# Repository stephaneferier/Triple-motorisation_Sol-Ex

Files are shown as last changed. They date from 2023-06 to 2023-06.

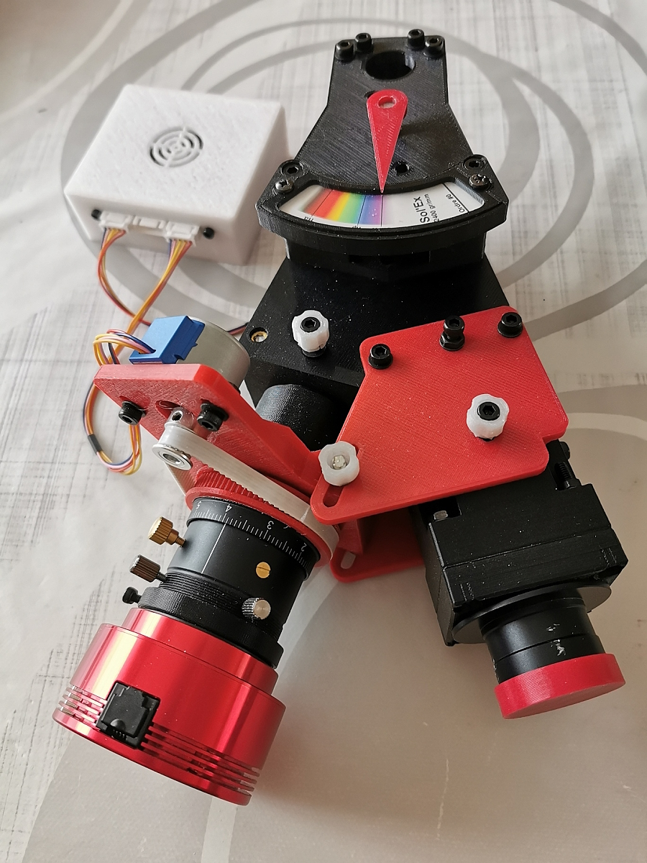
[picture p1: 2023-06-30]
focuser caméra.jpg

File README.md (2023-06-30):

# SolEx Motorisation (English version below)

Le Sol'Ex de Christian Buil est un "Explorateur solaire" qui permet d'imager le soleil dans une longueur d'onde souhaitée, allant du proche UV au proche IR.
La construction de ce spectroscope est détaillée sur son site internet: http://www.astrosurf.com/solex/sol-ex-objet.html
La partie traitement informatique du signal enregistré est confiée soit à i-Spec (programme écrit par Christian Buil), soit par Inti, programme développé par Valérie Desnoux. Ces deux programmes sont référencés sur le site Sol'Ex, et des mises à jour régulières sont publiées.
Un forum d'échange est aussi disponible à l'adresse : https://groups.io/g/Solex-project La communauté y est très active.

Nous vous présentons ici un appendice développé conjointement par Jean Brunet, Pascal Berteau et Stéphane Ferier, qui permet de motoriser le Sol'Ex initial, ainsi que la prise en charge de la mise au point de la lunette astro et du focuseur hélicoïdal de la caméra d'acquisition!
Le but ici est d'apporter une facilité à voyager parmi les raies spectrales qui composent le spectre solaire, au moyen d'un software développé pour Android/IOS, basé sur une page web gérée par le software. Des raies spectrales d'intérêt majeur y sont définies, et accessibles d'un simple clic.

Le programme ainsi que les fichiers .stl de construction du support de motorisation sont "open-source", et toute amélioration est la bienvenue.
Pour un complément d'informations sur la manière d'uploader les fichiers .ino dans l'ESP, veuillez trouver les informations utiles sur le projet initial "Motorisation du Sol'Ex" disponible ici: https://github.com/stephaneferier/SolEx-Motorisation
Vous y trouverez un fichier .pdf qui décrit en détails comment réaliser cette motorisation, comment monter le système sur le Sol'Ex, comment réaliser le montage électronique de pilotage, comment uploader le software dans l'ESP32 utilisé, ainsi que coment utiliser le software. Ce fichier .pdf est disponible en Français, et en Anglais.

# SolEx Motorization (English Version)

Christian Buil's Sol'Ex is a "solar explorer" which allows the sun to be imaged in a desired wavelength, ranging from near UV to near IR.
The construction of this spectroscope is detailed on its website: http://www.astrosurf.com/solex/sol-ex-objet.html
The computer processing part of the recorded signal is entrusted either to i-Spec (program written by Christian Buil), or by Inti, program developed by Valérie Desnoux. These two programs are referenced on the Sol'Ex site, and regular updates are published.
An exchange forum is also available at: https://groups.io/g/Solex-project The community is very active there.

We present here an appendix developed jointly by Jean Brunet, Pascal Berteau and Stéphane Ferier, which makes it possible to motorize the initial Sol'Ex, as well as the management of the focusing of the astro telescope and the helical focuser of the camera. acquisition!
The goal here is to facilitate travel among the spectral lines that make up the solar spectrum, using software developed for Android/IOS, based on a web page managed by the software. Spectral lines of major interest are defined there, and accessible with a simple click.

The program as well as the motorization support construction .stl files are "open-source", and any improvement is welcome.
For more information on how to upload .ino files in the ESP, please find the useful information on the initial project "Motorization of the Sol'Ex" available here: https://github.com/stephaneferier/ SolEx-Motorization
You will find a .pdf file that describes in detail how to make this motorization, how to mount the system on the Sol'Ex, how to make the electronic pilot assembly, how to upload the software in the ESP32 used, as well as how to use the software. . This .pdf file is available in French and English.

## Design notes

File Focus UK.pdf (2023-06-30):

## Sol'Ex, camera focus with stiffeners

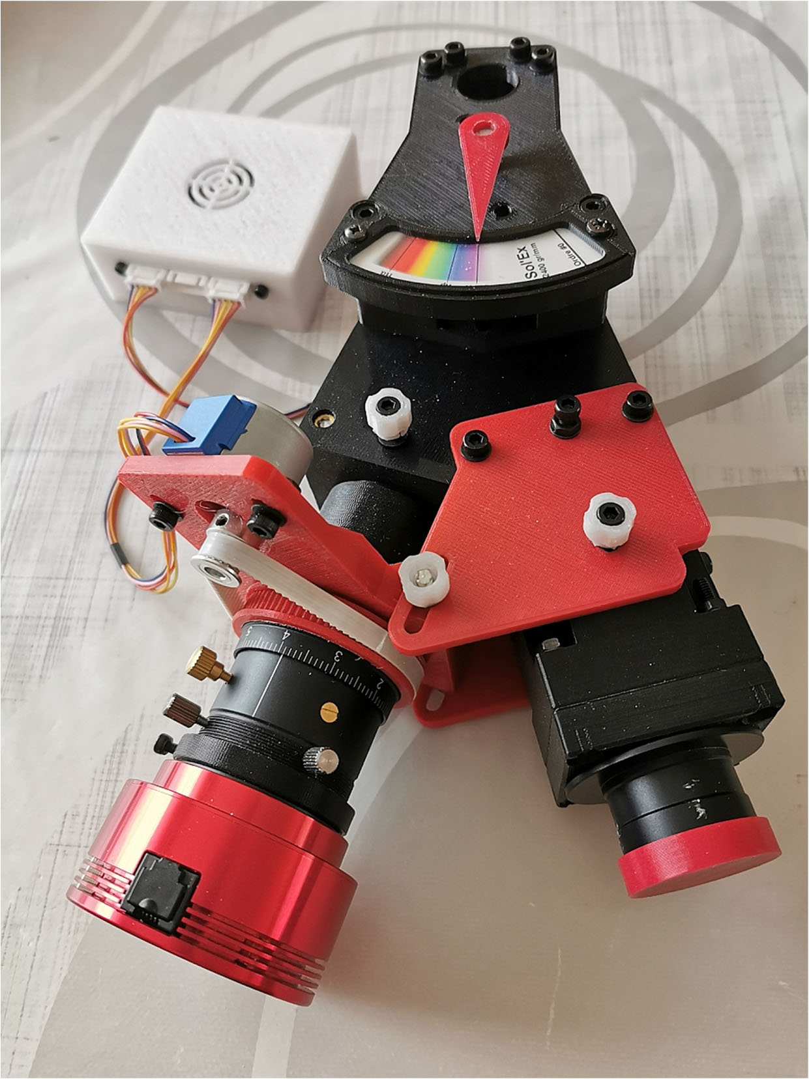
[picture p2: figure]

On the left the motor control box
The focuser has two functions, stiffening Sol'Ex and supporting the engine.

The fixation including the two symmetrical plates and the ring on the ZWO helical eyepiece holder was proposed on the Sol'Ex list by Gilles Leroy.
https://drive.google.com/drive/folders/1wKxa_FFrP0awlb0r-Le1xkUWJgxMOKyo

The GT2 belt wheel comes from Julien Lecomte's focuser also seen on the list. GitHub - jlecomte/ascom-oag-focuser: Open Source ASCOM-Compatible OAG Focuser For Astrophotography

I chose the belt drive for more precision.

I took the ring from the ZWO and added the motor mount. There is a 4mm ruthex on the side to secure the motor ring. A threaded rod encloses the two symmetrical stiffeners with the motor support ring. It will probably be necessary to play a little with sandpaper to adjust the two rings as not to have movement.

The turntable supports the 28BYJ-48 engine on which a small GT 2 sprocket is added. A GT2 belt 6 mm wide and 200 mm long connects the gear wheel to the engine.
The motor is fixed with two screws and two washers. The nuts are on the engine side that blocks them. Tighten the belt moderately when mounting so as not to weaken the small engine.

Good achievement to all,
Jean Brunet, Pascal Berteau, Stéphane Ferier.

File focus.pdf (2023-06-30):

## Sol'Ex, focuser caméra avec raidisseurs


A gauche le boîtier de commande des moteurs
Le focuser a deux fonctions, rigidifier Sol'Ex et supporter le moteur.

La fixation incluant les deux platines symétriques et la bague sur le porte oculaire hélicoïdal ZWO a été proposée sur la liste Sol'Ex par Gilles Leroy.
https://drive.google.com/drive/folders/1wKxa_FFrP0awlb0r-Le1xkUWJgxMOKyo

La roue pour courroie GT2 vient du focuser de Julien Lecomte vu aussi sur la liste.
GitHub - jlecomte/ascom-oag-focuser: Open Source ASCOM-Compatible OAG Focuser For Astrophotography
J'ai choisi la transmission par courroie pour plus de précision.

J'ai repris la bague du ZWO et j'ai ajouté le support du moteur. Il y a un ruthex de 4 mm sur le côté pour fixer la bague du moteur. Une tige filetée enserre les deux raidisseurs symétriques avec la bague support moteur. Il faudra sans doute un peu jouer du papier de verre pour ajuster les deux bagues qui ne doivent pas avoir de jeu.

La platine supporte le moteur 28BYJ-48 sur lequel on ajoute un petit pignon GT2. Une courroie GT2 de 6 mm de large et de 200 mm de long relie la roue dentée au moteur.
La fixation du moteur se fait avec deux vis et deux rondelles. Les écrous sont du côté du moteur qui les bloque. Tendre modérément la courroie au montage pour ne pas fragiliser le petit moteur.

Bonne réalisation à tous,
Jean Brunet, Pascal Berteau, Stéphane Ferier.

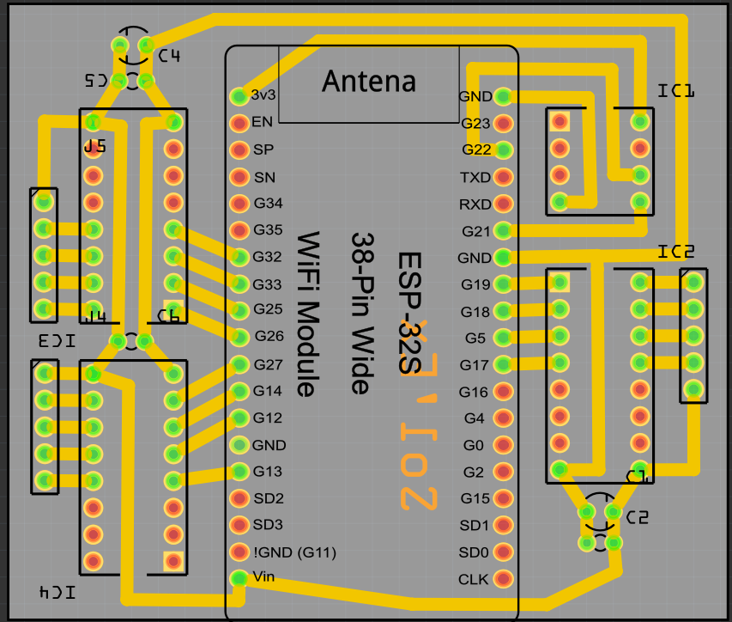
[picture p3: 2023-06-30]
Typon.png

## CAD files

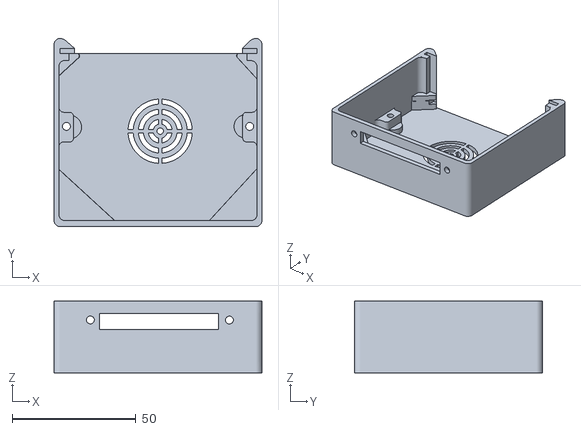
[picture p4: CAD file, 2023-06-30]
boitier3m.stl
84.1 x 76.1 x 29.1

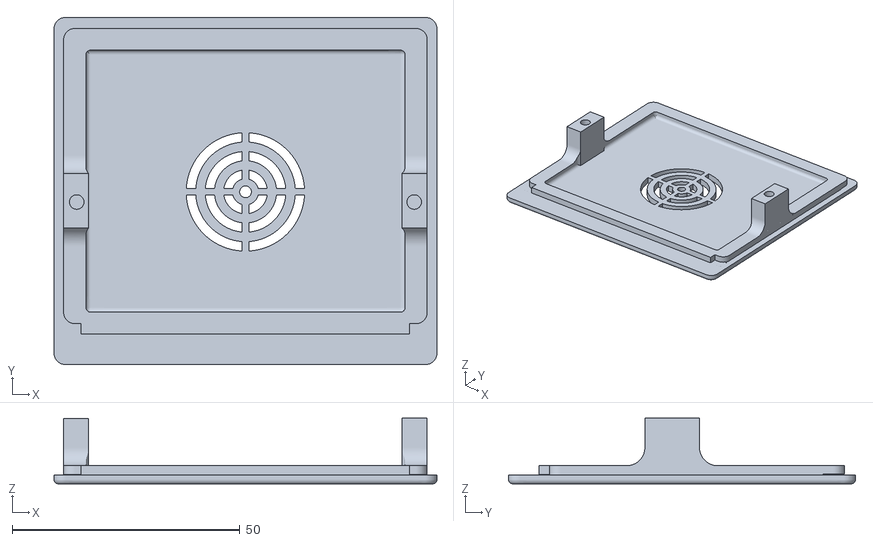
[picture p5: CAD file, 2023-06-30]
couvercle3m.stl
84.1 x 76.2 x 14.5

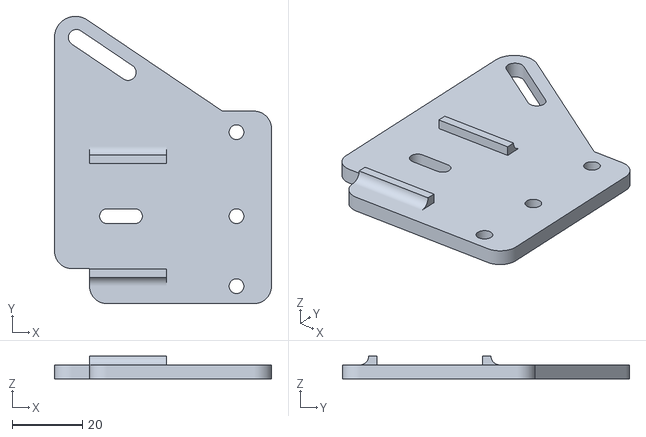
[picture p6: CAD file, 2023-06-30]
Renfort__Side_B_ZWO.stl
62.0 x 82.1 x 6.50

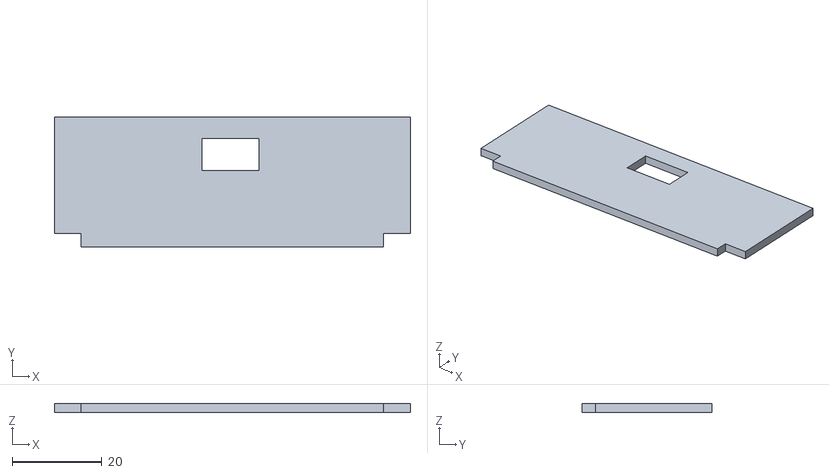
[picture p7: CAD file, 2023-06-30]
face3m.stl
79.4 x 29.0 x 2.00

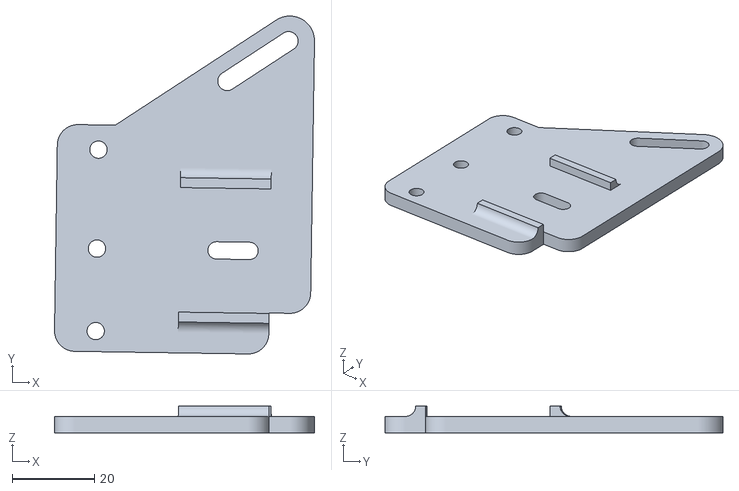
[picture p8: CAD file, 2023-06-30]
Renfort__Side_A_ZWO.stl
63.1 x 81.9 x 6.50

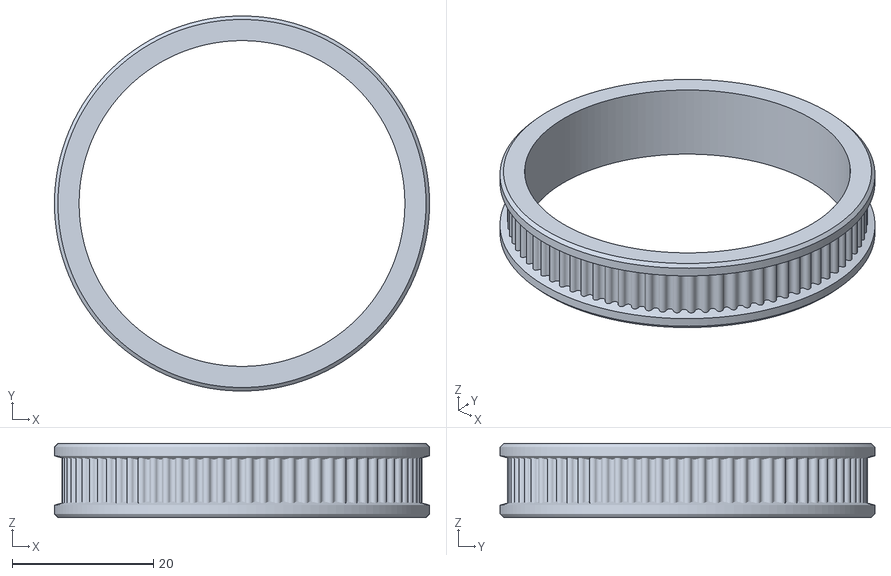
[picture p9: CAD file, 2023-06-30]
Focuser_Pulley.stl
53.2 x 53.2 x 10.5

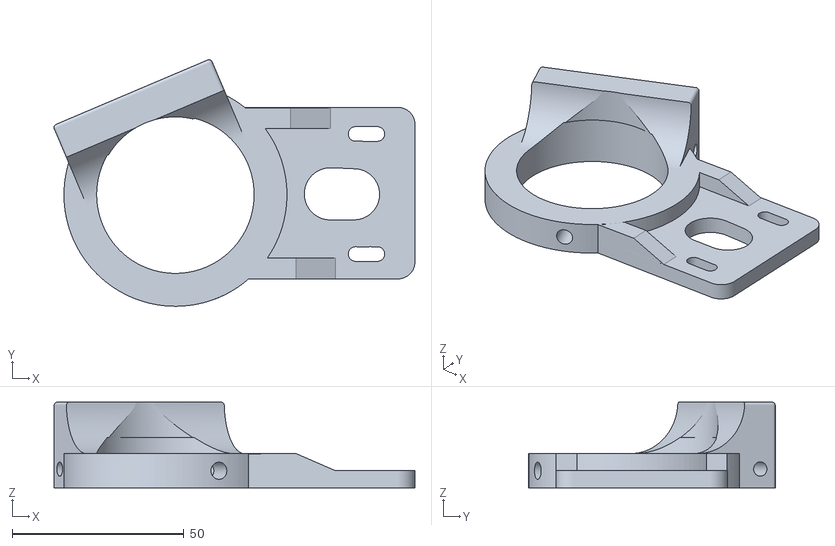
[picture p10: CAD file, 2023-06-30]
platine moteur.stl
105.2 x 71.9 x 25.0

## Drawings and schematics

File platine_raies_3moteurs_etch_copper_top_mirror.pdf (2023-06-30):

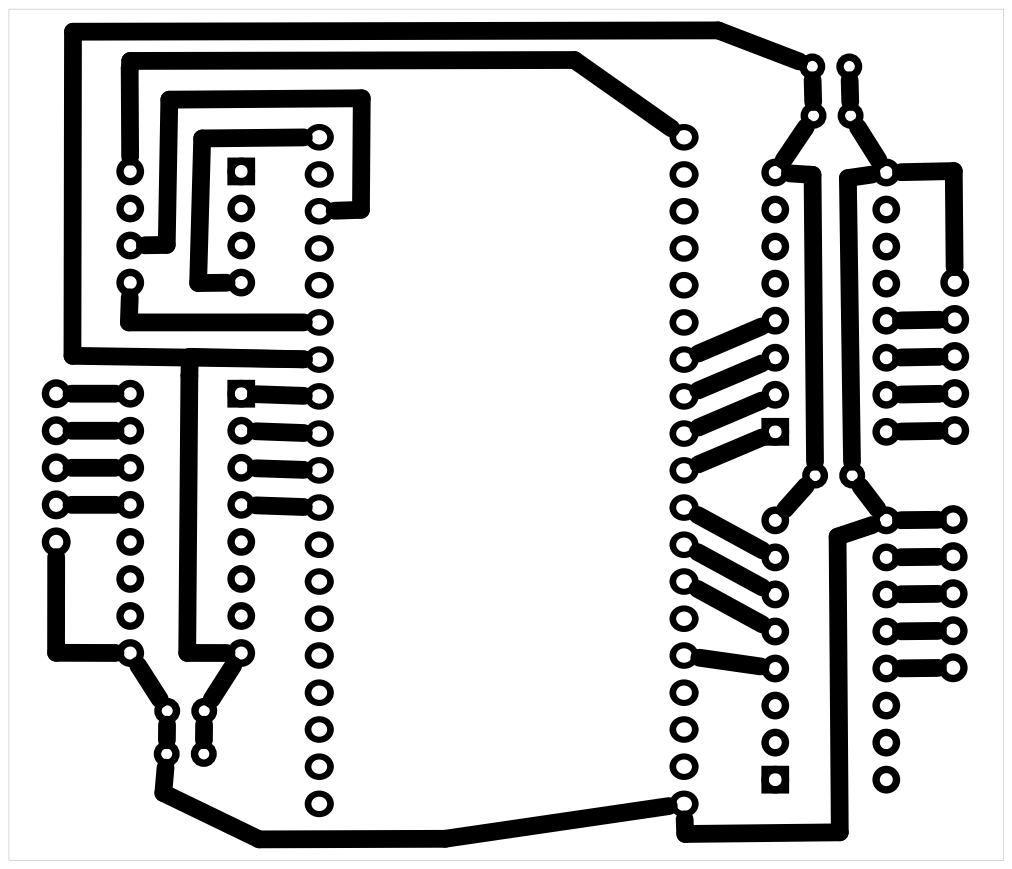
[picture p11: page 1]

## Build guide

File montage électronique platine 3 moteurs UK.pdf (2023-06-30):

Electronic stage with 3 motors

PCB assembly

You will find in the sharing the typons of the printed circuit boards in pdf format for those who wish to order the circuits (see the possible resellers on the internet) or engrave them themselves by sunstroke. For those who have a PCB burner, these files are also provided in Gerber format.

Once in possession of the printed circuit boards, assembly can begin.

Take the plates supplied with the motors and remove the ULN2003 ICs, desolder the IC bracket and the white connector. However, I give a list of all the components to buy from Conrad. The ESP32 DEV Kit is available on Amazon.

Start by soldering the 8-pin and 16-pin IC brackets, then solder the ESP32's two support strips. Finish with the capacitors, pay attention to the direction of chemical capacities, on the photo the positive (+) is indicated. Weld the 3 clusters of 5 wires at the output of the ULN 2003.

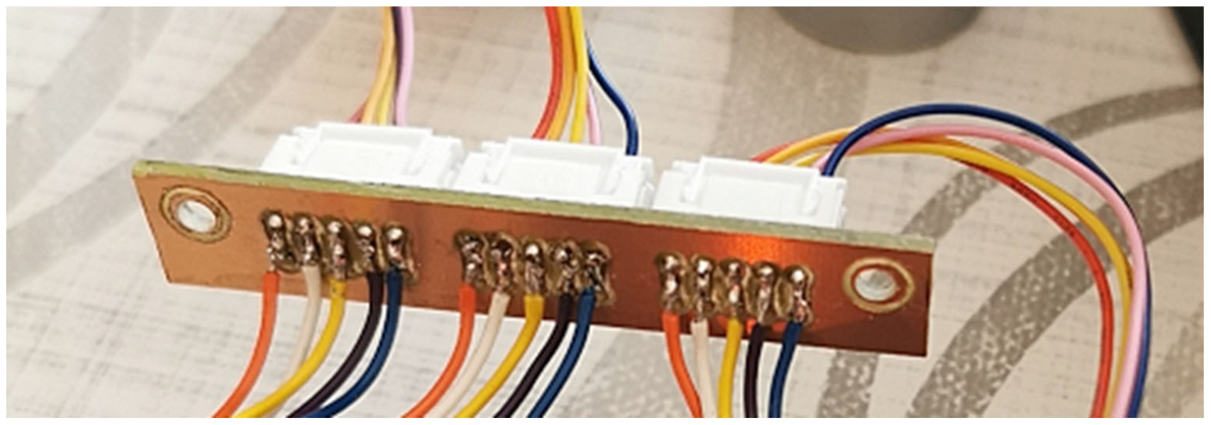
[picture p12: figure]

The connectors are to be welded in the alignment of the two screw holes, keying upwards. The wires are soldered directly onto the tracks of the mini circuit board.

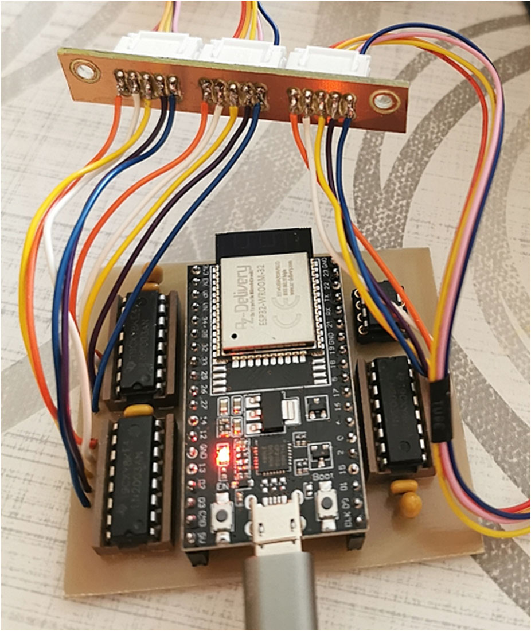
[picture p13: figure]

Take care to respect the order of the threads
according to their color. Orange is the +
noted on the typon.

Place ULN 2003 and 24LC01 on
their supports, pin 1 is
identified on the typon (see below). the

ESP32 is to place the USB connector directed outside of the printed circuit board.

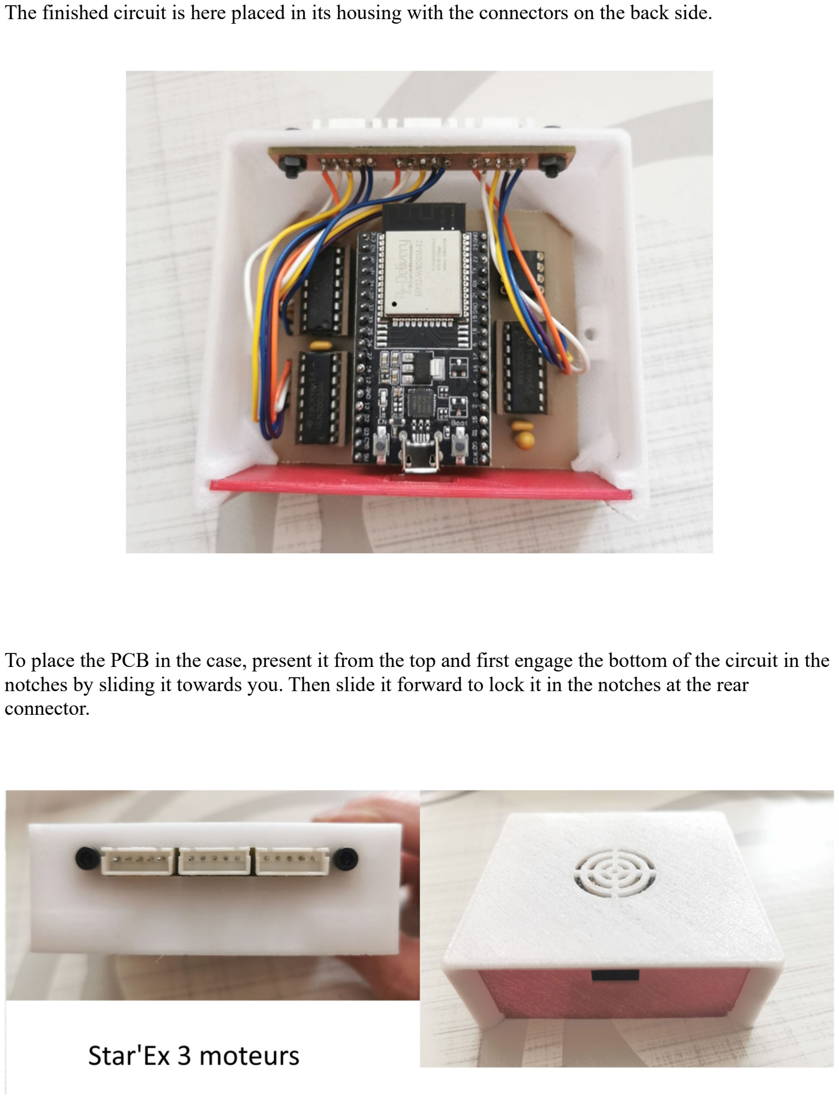
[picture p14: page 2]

The finished circuit is here placed in its housing with the connectors on the back side.

To place the PCB in the case, present it from the top and first engage the bottom of the circuit in the notches by sliding it towards you. Then slide it forward to lock it in the notches at the rear connector.

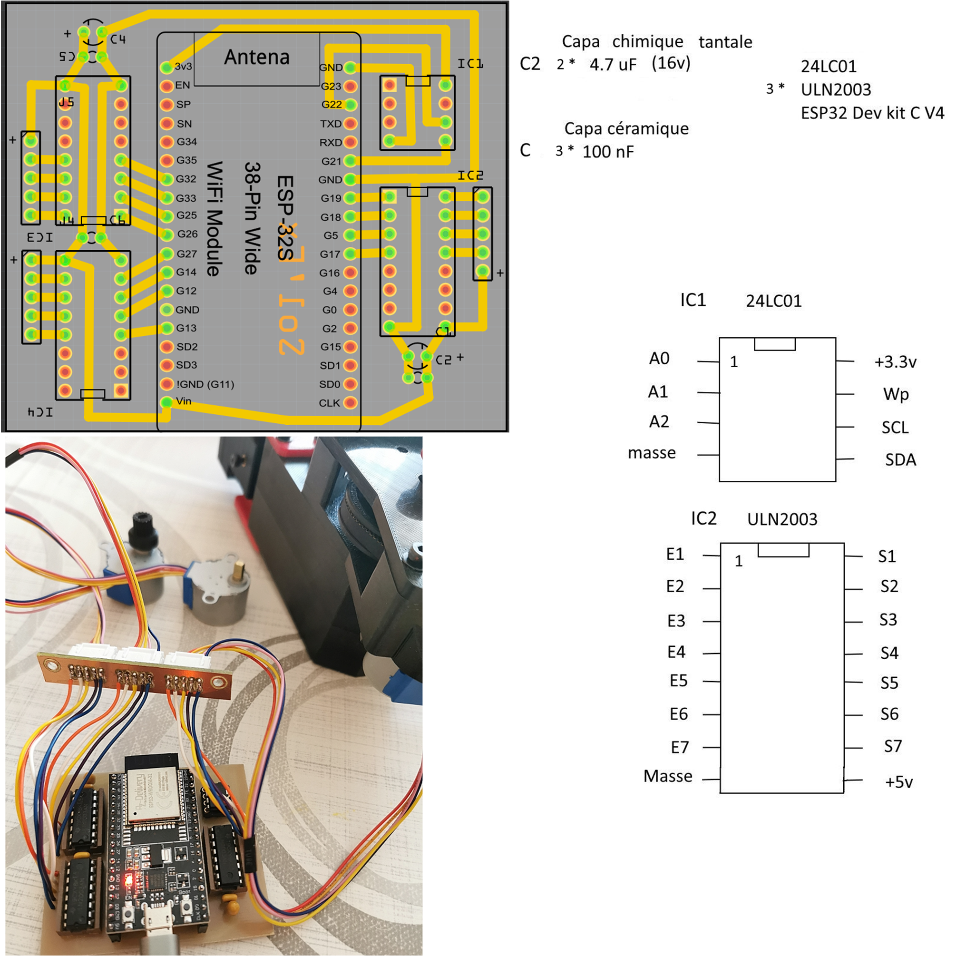
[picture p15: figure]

List of components to buy from Conrad (or other dealers of your choice).

3 * 100 nF Kemet C320C104M5U5TA+ 100 nF 50 V 20 % Z5U 1 pc(s) - Conrad Electronic France

2 * 4.7 uF TANCAP CA42-475M035AB Tantalum Capacitor THT 2.5 mm 4.7 μF 35 V 20% (W x
H) 5.5 mm x 14 mm 1 pc(s) - Conrad Electronic France

8-pin bracket Integrated circuit holder 7.62 mm, 2.54 mm Number of poles (num): 8 precision contacts 1 pc(s) - Conrad Electronic France

3 * 16-pin Support econ connect Integrated Circuit Support Number of poles (num): 16 precision contacts 1 pc(s) Tube - Conrad Electronic France

Strips for ESP32 (provide two) Connfly Female bar (standard) Number of rows: 1 Number of poles per row: 20 DS1023-1*20S21 1 pc(s) - Conrad Electronic France

24LC01 Microchip Technology 24LC01B/P CI Memory DIP-8 EEPROM 1 ko 128 x 8 - Conrad Electronic France

3 * ULN2003 STMicroelectronics Transistor dipolar (BJT) - Matrix ULN2003A DIP-16 7 NPN -Darlington - Conrad Electronic France

3 * 5-pin Connector Male Case (Turntable) econ connect W33S5 Total Bbr Poles 5 Steps: 2.5 mm 1 pc(s) - Conrad Electronic France

ESP32-WROOM-32 Dev kit C4: https://www.amazon.fr/dp/B08BTS62L7

Good achievement to all,
Jean Brunet
Pascal Berteau
Stéphane Ferier

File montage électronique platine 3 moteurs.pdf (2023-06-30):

Platine électronique avec 3 moteurs

Montage du circuit imprimé

Vous trouverez dans le partage les typons des circuits imprimés au format pdf pour ceux qui souhaitent commander les circuits (voir les éventuels revendeurs sur internet) ou les graver euxmêmes par insolation. Pour ceux qui ont une graveuse de circuit imprimé, ces fichiers sont aussi fournis au format Gerber.

Une fois en possession des circuits imprimés, on peut entamer le montage.

Prendre les platines fournies avec les moteurs et retirez les circuits intégrés ULN2003, dessoudez le support du circuit intégré et le connecteur blanc. Toutefois, je donne une liste de tous les composants à acheter chez Conrad. L'ESP32 DEV Kit est disponible sur Amazon.

Commencez par souder les supports des circuits intégrés 8 broches et 16 broches, puis soudez les deux barrettes support de l'ESP32. Terminez par les condensateurs, attention au sens des capacités chimiques, sur la photo le positif (+) est indiqué. Soudez les 3 grappes de 5 fils en sortie des ULN 2003.

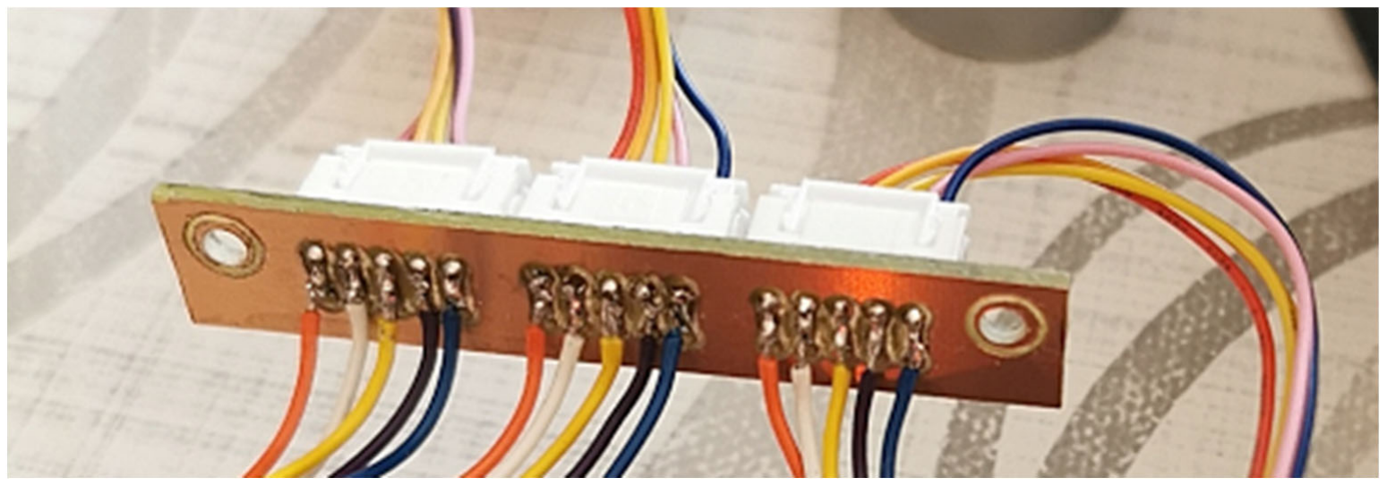
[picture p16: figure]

Les connecteurs sont à souder dans l'alignement des deux trous de vis, détrompeurs vers le haut. Les fils sont soudés directement sur les pistes
du mini circuit imprimé.

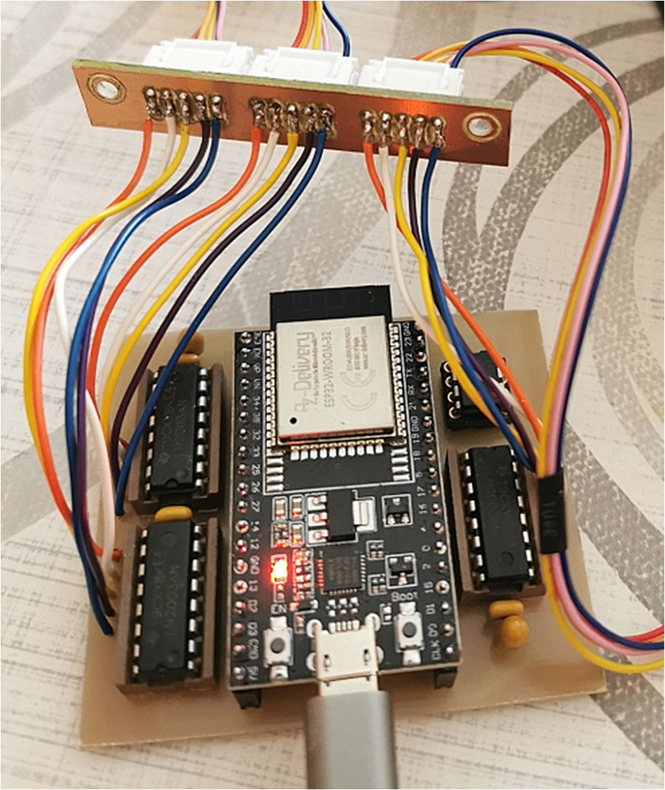
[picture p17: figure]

Bien respecter l'ordre des fils
selon leur couleur. Le orange est le +
noté sur le typon.

Placez les ULN 2003 et le 24LC01 sur leurs supports, la broche 1 est identifiée sur le typon (voir ci-dessous).

l'ESP32 est à placer le connecteur USB vers le bas du circuit imprimé.

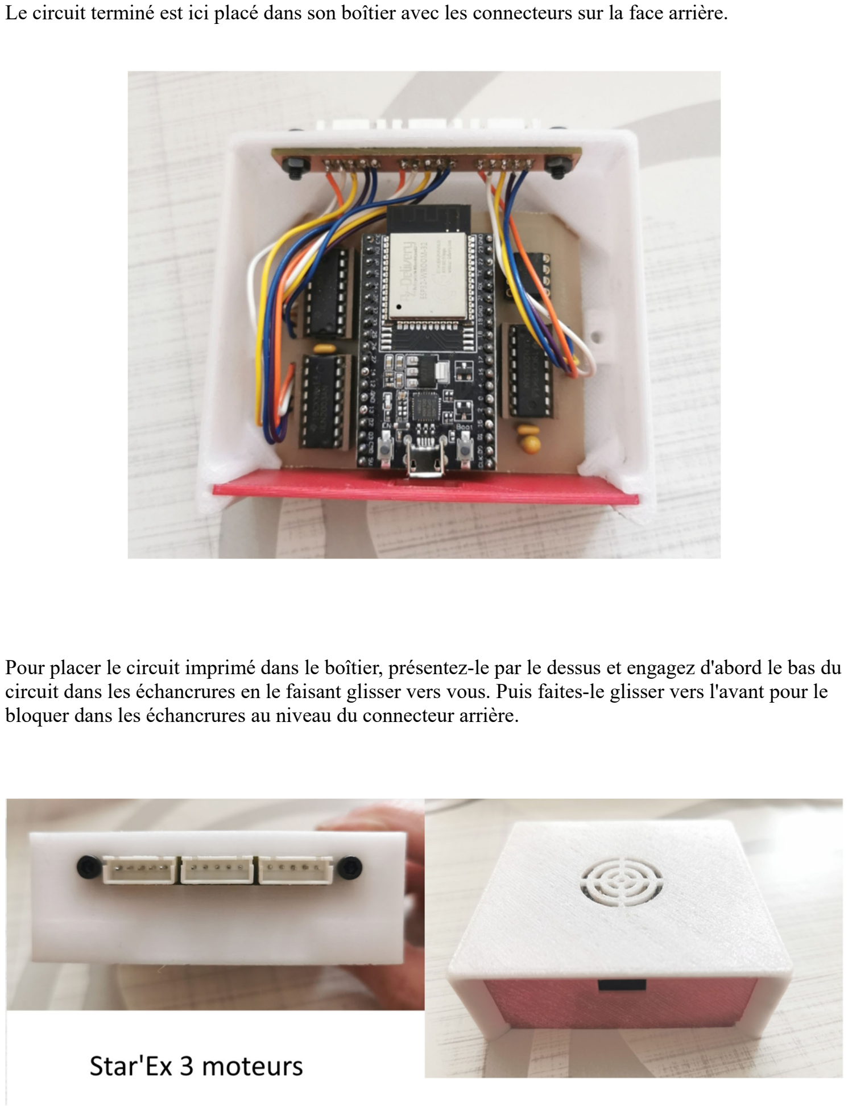
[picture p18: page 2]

Le circuit terminé est ici placé dans son boîtier avec les connecteurs sur la face arrière.

Pour placer le circuit imprimé dans le boîtier, présentez-le par le dessus et engagez d'abord le bas du circuit dans les échancrures en le faisant glisser vers vous. Puis faites-le glisser vers l'avant pour le bloquer dans les échancrures au niveau du connecteur arrière.


Liste des composants à acheter chez Conrad (ou d'autres revendeurs de votre choix).

3 * 100 nF Condensateur céramique sortie radiale Kemet C320C104M5U5TA+ 100 nF 50 V 20 % Z5U 1 pc(s) - Conrad Electronic France

2 * 4,7 uF TANCAP CA42-475M035AB Condensateur tantale THT 2.5 mm 4.7 µF 35 V 20 % (l x
H) 5.5 mm x 14 mm 1 pc(s) - Conrad Electronic France

Support 8 broches Support de circuits intégrés 7.62 mm, 2.54 mm Nombre de pôles (num): 8 contacts de précision 1 pc(s) - Conrad Electronic France

3 * Support 16 broches econ connect Support de circuits intégrés Nombre de pôles (num): 16 contacts de précision 1 pc(s) Tube - Conrad Electronic France

Barrettes pour l'ESP32 (en prévoir deux) Connfly Barrette femelle (standard) Nbr de rangées: 1

Nombre de pôles par rangée: 20 DS1023-1*20S21 1 pc(s) - Conrad Electronic France

24LC01 Microchip Technology 24LC01B/P CI Mémoire DIP-8 EEPROM 1 ko 128 x 8 - Conrad Electronic France

3 * ULN2003 STMicroelectronics Transistor bipolaire (BJT) - Matrice ULN2003A DIP-16 7 NPN -Darlington - Conrad Electronic France

3 * Connecteur 5 broches Boîtier mâle (platine) econ connect W33S5 Nbr total de pôles 5 Pas: 2.5 mm 1 pc(s) - Conrad Electronic France

ESP32-WROOM-32 Dev kit C4: https://www.amazon.fr/dp/B08BTS62L7

Bonne réalisation à tous,
Jean Brunet
Pascal Berteau
Stéphane Ferier

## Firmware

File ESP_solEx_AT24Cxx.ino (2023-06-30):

// programme pour le Sol'Ex (solar explorer) de Christian Buil.
// version originale : Jean Brunet  le 17/01/2023 écrite pour commander le déplacement du réseau.

// Cette nouvelle version a été réécrite depuis le 22/04/2023 par Pascal Berteau avec 5 raies programmées 
// et la commande de 3 moteurs, réseau, focus caméra et focus lunette.
// Le programme a été l'objet de nombreux ajouts par Jean Brunet et Pascal Berteau pour finalement
// aboutir à celui-ci.

// La position des raies est mémorisée, ainsi que la position du focus caméra en appuyant sur Mémo.
// Le couplage des moteurs réseau et focus caméra permet de se positionner sur une raie en obtenant automatiquement la netteté.
// Ainsi il n'y a pas besoin d'intervenir manuellement sur Sol'Ex, ni sur la lunette de visée qui utilise le troisième moteur.

// Ce programme est à choisir pour un module AT24Cxx
// Si vous utilisez la mémoire EEPROM 24LC01B, prenez le programme ESP32_SolEx_24LC01B.ino

// Pascal Berteau, Jean Brunet - le 12 / 06 /2023. Ce programme peut être distribué librement.

// IMPORTANT !!
#define initmemo 0  // Mettre à 1 pour la première utilisation pour initialisation de la mémoire. Ensuite mettre initmemo à 0

#include <WiFi.h>
#include <WiFiClient.h>
#include <WiFiServer.h>
#include <WiFiUdp.h>
#include <WiFi.h>
#include <AT24Cxx.h>  // bibliothèque à installer dans arduino

#define MOTOR2_PIN_1  32   // Blue   - 28BYJ48 pin 1
#define MOTOR2_PIN_3  33  // Pink   - 28BYJ48 pin 2
#define MOTOR2_PIN_2   25  // Yellow - 28BYJ48 pin 3
#define MOTOR2_PIN_4  26   //  Orange - 28BYJ48 pin 4

#define MOTOR3_PIN_1  27   // Blue   - 28BYJ48 pin 1
#define MOTOR3_PIN_3  14  // Pink   - 28BYJ48 pin 2
#define MOTOR3_PIN_2   12  // Yellow - 28BYJ48 pin 3
#define MOTOR3_PIN_4  13   //  Orange - 28BYJ48 pin 4

#define MOTOR_PIN_1  19   // Blue   - 28BYJ48 pin 1
#define MOTOR_PIN_3  18  // Pink   - 28BYJ48 pin 2
#define MOTOR_PIN_2   5  // Yellow - 28BYJ48 pin 3
#define MOTOR_PIN_4  17   //  Orange - 28BYJ48 pin 4


int address = 0x50;

AT24Cxx eep(address, 32); // module AT24Cxx, mettre en Ko la longueur de l'EEPROM installée. Ici 32 Ko.

// raies programmées

unsigned int RAIEHa = 1230;
unsigned int RAIENa = 1060;
unsigned int RAIEMg = 910;
unsigned int RAIEHb = 850;
unsigned int RAIECa = 670;

const char* ssid = "SolEx";
const char* password = "solex1234";  // A MODIFIER si plusieurs Sol'Ex proches
WiFiServer server(80);

String header;
const unsigned int STEPZero = 0;  

const unsigned int STEPRes1 = 5;  
const unsigned int STEPRes2 = 25;  
const unsigned int STEPRes3 = 100;  

const unsigned int STEPCam1 = 5;  
const unsigned int STEPCam2 = 25; 

const unsigned int STEPFoc1 = 5;  
const unsigned int STEPFoc2 = 25;
const unsigned int STEPFoc3 = 200;  

const unsigned int Backlash_Res = 15;  
const unsigned int Backlash_Cam = 15 + 25;  // jeux pignons (15) et jeux focus hélicoïdal. (25) A ajuster si besoin    
const unsigned int Backlash_Foc = 15;  

unsigned int STEPREL = 0;
unsigned int indice_ray_select = 0;

const unsigned long STEP_DELAY_MICROSEC = 5000;  // vitesse moteur
int cycle = 0;
int cycle2 = 0;
int cycle3 = 0;

bool direction = true;
bool dir_Cam = true;
bool dir_Foc = true;
bool dir_Res = true;

int positionRes = 0;
int positionCam = 0;
int positionFoc = 0;
unsigned long last_step_time;

bool memo = false;
bool CouplageOk = false;
/* ---------------------------
setup
-------------------------------*/
void setup() 
{
    // Initialize serial port I/O.
    // Serial.begin(115200); // seulement pour déboggage

    // Initialize motor control pins...
    pinMode(MOTOR_PIN_1, OUTPUT);
    pinMode(MOTOR_PIN_2, OUTPUT);
    pinMode(MOTOR_PIN_3, OUTPUT);
    pinMode(MOTOR_PIN_4, OUTPUT);

    pinMode(MOTOR2_PIN_1, OUTPUT);
    pinMode(MOTOR2_PIN_2, OUTPUT);
    pinMode(MOTOR2_PIN_3, OUTPUT);
    pinMode(MOTOR2_PIN_4, OUTPUT);

    pinMode(MOTOR3_PIN_1, OUTPUT);
    pinMode(MOTOR3_PIN_2, OUTPUT);
    pinMode(MOTOR3_PIN_3, OUTPUT);
    pinMode(MOTOR3_PIN_4, OUTPUT);

    direction = true;
    dir_Cam = true;
    dir_Res = true;
    dir_Foc = true;
    
    last_step_time = 0L;
    WiFi.softAP(ssid, password);

    IPAddress IP = WiFi.softAPIP();
    server.begin();
    // lecture en mémoire EEPROM de la dernière position enregistrée.
    #if initmemo
     for(int i = 0 ; i < 30; i++){   // met la mémoire à 0 pour la première utilisation. Remettre initmemo à 0 ensuite
          eep.write(i, 0);
          delay(5);
     }
    indice_ray_select = 20;  positionRes = RAIEHa; WriteMemoryRes(indice_ray_select);
    indice_ray_select = 22;  positionRes = RAIENa; WriteMemoryRes(indice_ray_select);
    indice_ray_select = 24;  positionRes = RAIEMg; WriteMemoryRes(indice_ray_select);
    indice_ray_select = 26;  positionRes = RAIEHb; WriteMemoryRes(indice_ray_select);
    indice_ray_select = 28;  positionRes = RAIECa; WriteMemoryRes(indice_ray_select);
     #endif
    byte val1 = eep.read( 0);
    byte val2 = eep.read( 1);
    positionRes = word(val1, val2);
    cycle = eep.read( 2);
    dir_Res = eep.read( 3);

    val1 = eep.read( 4);
    val2 = eep.read( 5);
    positionCam = word(val1, val2);
    cycle2 = eep.read( 6);
    dir_Cam = eep.read(7); 
     
    val1 = eep.read( 8);
    val2 = eep.read( 9);
    positionFoc = word(val1, val2);
    cycle3 = eep.read( 10);
    dir_Foc = eep.read( 11);
}
 /* --------------------------------
Boucle de traitement
-------------------------------------*/
void loop() 
{
	Wificommmand();  // affichage de la page web et traitement des retours utilisateur
}


/*---------------------------------------------------------------------------------------------
 Page web et traitement des commandes envoyées par l'utilisateur
------------------------------------------------------------------------------------------------*/
void Wificommmand()
{

	WiFiClient client = server.available();   // Listen for incoming clients
  CouplageOk = false; 
	if (client){ 
   while (client.connected()){            // loop while the client's connected
		if (client.available()) {             // if there's bytes to read from the client,
			char c = client.read();             // read a byte, then
			header += c;
			if (c == '\n') // si c'est la fin de la commande reçue
			{          
				client.println("HTTP/1.1 200 OK");
				client.println("Content-type:text/html");
				client.println("Connection: close");
				client.println();
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
